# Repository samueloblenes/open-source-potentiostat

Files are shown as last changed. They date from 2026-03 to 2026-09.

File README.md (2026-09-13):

# Open-Source Potentiostat

**A fully open-source, low-cost potentiostat for electrochemical characterization, built as an alternative to commercial instruments.**

> **Status: Active development.** Not yet complete or ready for use. See [Build Progress](#build-progress) below for current status.

---

## Overview

This project is an attempt to build a fully open - hardware, firmware, and software - potentiostat capable of electrochemical characterization, at a fraction of the cost of a comercial instrument.

The instrument is built around a three-electrode electrochemical cell, using a potentiostatic control loop to maintain a precise potential and a switchable-gain transimpedance amplifier to measure the resulting current. A Teensy 4.1 handles low-level control and data acquisition, with a Python-based GUI for control and data analysis.

Once complete, the instrument will be validated against published cyclic voltammetry data.

## Build Progress

- [x] Circuit design
- [x] SPICE simulation
- [x] Preliminary firmware
- [x] Breadboard prototype
- [x] Enclosure design 
- [ ] Breadboard testing & debugging *(in progress)*

<p float="left">
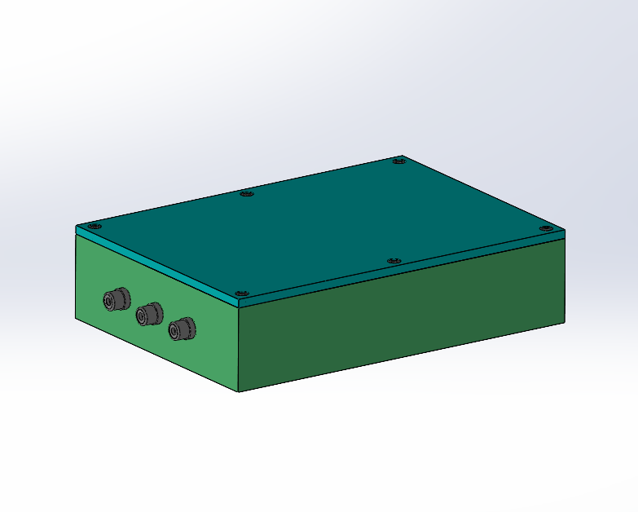
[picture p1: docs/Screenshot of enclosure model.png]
  
</p>

<p float="left">
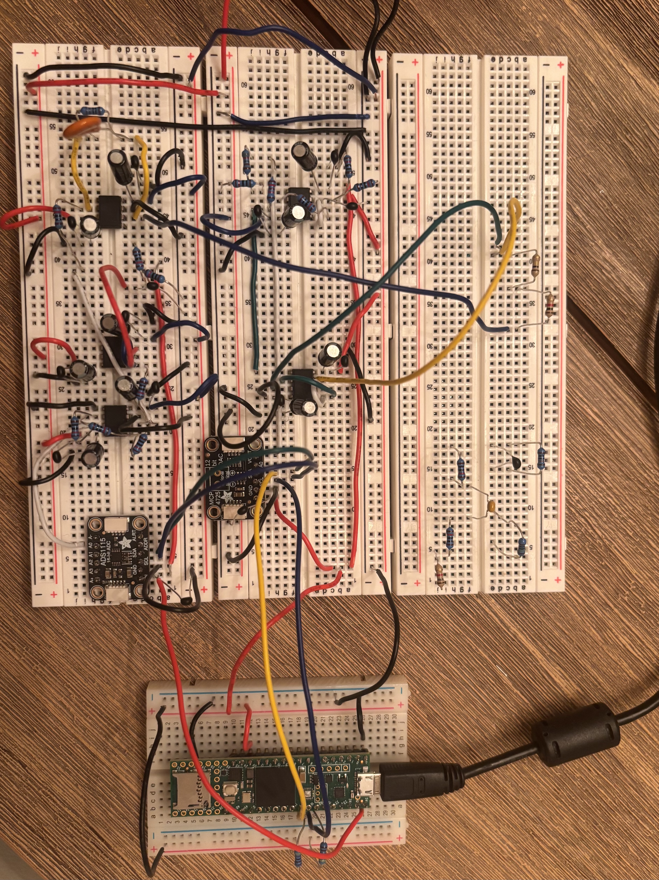
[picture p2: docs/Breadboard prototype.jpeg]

</p>

## Repository Structure
```
open-source-potentiostat/
├── firmware/                
│   └── firmware.ino         
├── hardware/                
│   ├── schematic/           
│   └── simulation/          
├── software/                
│   ├── app.py
│   ├── main.py
│   └── requirements.txt
├── docs/                    
│   ├── BOM.csv
│   ├── circuit_design_notes.md
│   └── simulation_notes.md
├── LICENSE_hardware
├── LICENSE_software
└── README.md
```
## Acknowledgments

This project draws inspiration from **CheapStat**, an open-source, "do-it-yourself" potentiostat originally designed by Aaron Rowe, Andrew Bonham, Michael Zimmer, Kevin Plaxco and colleagues at UC Santa Barbara, which demonstrated that a fully open, low-cost potentiostat could support real analytical and educational applications.

- Rowe, A.A., Bonham, A.J., White, R.J., et al. (2011). ["CheapStat: An Open-Source, 'Do-It-Yourself' Potentiostat for Analytical and Educational Applications."](https://doi.org/10.1371/journal.pone.0023783) *PLOS ONE*.

## License

- Hardware design files: [CERN-OHL-S v2](https://ohwr.org/cern_ohl_s_v2.txt)
- Software and firmware: MIT

## Author

**Samuel O'Blenes**
GitHub: [@samueloblenes](https://github.com/samueloblenes)

---

*This is a work in progress - design files, firmware, and documentation will be updated as the project develops. Feedback and suggestions are welcome via GitHub Issues.*

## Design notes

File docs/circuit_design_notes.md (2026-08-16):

# Component Selection and Circuit Design

## Overview
This document describes the circuit design of the open-source potentiostat, The design priorities are affordability, reproducibility, and sufficient performance.

## Design requirements and constraints

### Functional requirements
CV - Cyclic Voltammetry:
The working electrode potential is swept linearly from an initial value to a final value, then reversed back to the initial value. Current at the working electrode is measured continuously as a function of applied potential. Used for characterizing oxidation and reduction reactions, corrosion behaviour, reaction reversibility, etc.

LSV - Linear Sweep Voltammetry
The working electrode potential is swept linearly from an initial value to a final value in one direction only, with no reverse scan. Current is measured continuously during the sweep.

CA - Chronoamperometry
The working electrode potential is stepped to a value and held constant while current at the working electrode is measured as a function of time. Used for studying reaction kinetics.

### Performance requirements
The instrument must operate within a voltage, current, and scan rate range sufficient to perform the electrochemical techniques described in Section 2.1.

Potential Range:
A potential control range of ±2V was selected to cover all planned experiments with comfortable margin while keeping circuit complexity and cost minimal.

Current Measurement Range:
The working electrode current during the planned experiments spans approximately from 10 nA to 2 mA. Four switchable transimpedance gain ranges (1 kΩ, 10 kΩ, 100 kΩ, 1 MΩ) were selected to cover this range with adequate resolution at each decade.

Resolution and Accuracy:
In order to have sufficient accuracy, the following minimum resolution specifications were established:
- current resolution less than 1 nA
- voltage resolution at least 1 mV
- ADC resolution at least 16-bit
- potential accuracy of ± 5mV

### Cost and accessibility constraints
- Cost should be kept under $200
- Components must be available from major suppliers
- Assembly should be relatively simple and require hand soldering only

## Component selection and circuit design

### Microcontroller

#### Microcontroller consideration
The microcontroller must satisfy the following requirements:
- Sufficient processing speed for precise sweep timing across the full scan rate range of 1 mV/s to 500 mV/s without timing jitter that would distort CV curve measurements.
- Hardware I2C and SPI peripherals for communication with the DAC and ADC.
- A regulated 3.3V output and a 5V output.
- Compatibility with the Arduino IDE to maximise accessibility and reproducibility.

#### Microcontroller selection
The Teensy 4.1 was selected. It operates at 600 MHz with an ARM Cortex-M7 processor, providing sufficient processing speed, and is fully compatible with the Arduino IDE via the Teensyduino add-on. I2C and SPI peripherals are available for communication with the DAC and ADC. The board provides a regulated 3.3V output and a 5V VUSB output. It does not include an onboard DAC; this is addressed through the use of an external I2C DAC, which adds only one low-cost component to the design and has negligible impact on circuit complexity.

### DAC

#### DAC considerations
The Teensy 4.1 microcontroller does not include an onboard DAC, so an external DAC is required. The DAC receives a digital value from the Teensy and generates the analog voltage setpoint applied to the control loop, Vset. The DAC must have sufficient resolution to achieve at least 1mV per step, be able to cover the ±2V potential range, and be compatible with the Teensy 4.1 I2C interface.

#### DAC selection
The MCP4725 12-bit DAC was selected for this design. It operates from the Teensy 4.1's 3.3V supply. At 12-bit resolution over a 0 to 3.3V output range, the voltage step size is:

V = 3.3V / 2^12 = 0.806 mV/step

This meets the sub-mV resolution requirement. It is low cost, widely used and available, and breakout boards are widely available for breadboarding.

#### Bipolar output
The MCP4725 produces a unipolar output from 0V to 3.3V. The instrument must scan across negative potentials, so a bipolar potential range is required. A unipolar-to-bipolar converter circuit is placed between the DAC output and the control loop. A difference amplifier is used to shift and scale the DAC output to the required range.

For this circuit, a TL072 dual op-amp is used, with one channel as the differential amplifier and the other as a buffer for the 1.65V reference voltage.

The reference voltage is derived from an ADR4533 fixed 3.3V precision voltage reference IC, powered directly from the +12V rail. A matched 10kΩ:10kΩ resistor divider on the ADR4533's output sets the 1.65V midpoint, which is then buffered by the second TL072 channel. Per the ADR4533 datasheet, a minimum 0.1µF output capacitor and a 1µF/0.1µF input capacitor pair are required for stability and noise reduction.

Decoupling capacitors (100nF and 10µF) are placed on the ±12V rails to reduce noise, and a 100nF capacitor decouples the buffered reference voltage node.

### Potentiostatic control circuit
The potentiostatic control circuit receives the set voltage from the DAC, Vset, and maintains the potential in the cell at that value. To do this, the design uses another TL072 dual op-amp, with one channel configured as a reference buffer to read the reference electrode's potential without drawing any current from it, and the other as a control amplifier to maintain the potential in the cell equal to Vset.

### Transimpedance amplifier
The current from the working electrode must be converted into voltage so that the ADC can convert it to a digital signal. This is accomplished using a transimpedance amplifier (TIA). An OPA134 op-amp is used for its low input bias current. This is important because input bias current adds a fixed offset error to the measured current, which becomes significant at the nanoampere level. A feedback resistor is connected between the op-amp's inverting input and the output, and sets the transimpedance gain. The output voltage is determined by the product of the input current and the feedback resistance; for smaller currents a larger feedback resistance is required to get a voltage that the ADC can read. Decoupling capacitors (100nF and 10µF) are placed on the ±12V rails to reduce noise. A feedback compensation capacitor connected in parallel with the feedback resistor prevents oscillations caused by the phase shift introduced by cable capacitance. 

#### Gain switching
To accommodate the current ranges specified above, a DG441 quad analog switch allows switching between four feedback resistances of 1 kΩ, 10 kΩ, 100 kΩ, and 1 MΩ. Each switch is controlled by a different GPIO pin on the Teensy; setting a pin high closes the corresponding switch, completing the circuit between the op-amp's inverting input and the desired feedback resistor, which is connected to the output. This circuit is shown in Figure 5.

A 50 pF compensation capacitor is placed in parallel with the feedback resistors to prevent oscillation caused by the phase shift introduced by the input capacitance. This value was determined by AC stability simulation across all four gain ranges.

#### TIA output offset
The TIA output is bipolar, but the ADC requires a unipolar input within its supply range. An offset is applied using a weighted summing amplifier circuit after the TIA.

The first stage is an inverting summing amplifier that adds a 2.5V offset to the TIA output, shifting the signal range upward while inverting its polarity. The second stage is an inverting unity-gain amplifier that restores the correct polarity. The combined effect is a non-inverting +2.5V shift, placing the full output range within the ADC input window.

The 2.5V reference for the summing stage is supplied directly by an ADR4525 fixed 2.5V precision voltage reference IC, powered from the +12V rail. Per the ADR4525 datasheet, a minimum 1.0µF output capacitor and a 1µF/0.1µF input capacitor pair are required for stability.

The 2.5V offset is subtracted in firmware to recover the true current value.

### ADC

#### ADC considerations
The analog-to-digital converter (ADC) digitises the TIA output voltage to be sent to the Teensy 4.1. The ADC must have a resolution of at least 16-bit to achieve the resolution specified above.

#### ADC selection
The ADS1115 16-bit ADC was selected. It shares the I2C bus with the MCP4725 DAC, and operates from the 5V VUSB pin. 

#### I2C pull-up resistors
The SDA and SCL lines require pull-up resistors to 3.3V for correct I2C operation. Two external 4.7 kΩ resistors are placed on the SDA and SCL nets.

### Power supply

#### +12V input and −12V generation
+12V is supplied externally via a barrel-jack input. The −12V rail required by the op-amps is generated from this +12V supply using a TC7662B switched-capacitor voltage inverter.

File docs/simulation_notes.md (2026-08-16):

# Simulation Notes
This document outlines the circuit simulations done during the design process. All simulations were done using LTspice, an open source SPICE simulation software. Simulation files can be found in the `simulations/` folder of this repository.

---

# 1. DAC Offset Circuit

**Purpose**
Verify that the difference amplifier correctly scales and shifts the MCP4725 unipolar output (0–3.3V) to the required bipolar range (±2V), confirming the resistor values R1 = 8.25 kΩ, R2 = 10 kΩ, R3 = 10 kΩ, R4 = 12.1 kΩ produce the correct output.

## 1.1 DC Operating Point

Expected results are calculated as follows:

```
Vout = (R4/R2) × (Vin - Vref)
Vout = (12.1k/10k) × (Vin - 1.65)
Vout = 1.21 × (Vin - 1.65)
```

**Test 1: Minimum input (Vin = 0V)**

Calculation: Vout = 1.22 × (0 - 1.65) = **-2.0V**

| Node | Expected | Simulated | Pass/Fail |
|------|----------|-----------|-----------|
| Vref | 1.65V | 1.64996V | Pass |
| Vout | -2.0V | -1.9997V | Pass |

Simulation file: `DAC_Offset_DC_PNT_1`

---

**Test 2: Midpoint input (Vin = 1.65V)**

Calculation: Vout = 1.22 × (1.65 - 1.65) = **0V**

| Node | Expected | Simulated | Pass/Fail |
|------|----------|-----------|-----------|
| Vref | 1.65V | 1.65V | Pass |
| Vout | 0V | 0.000110925V | Pass |

Simulation file: `DAC_Offset_DC_PNT_2`

---

**Test 3: Maximum input (Vin = 3.3V)**

Calculation: Vout = 1.22 × (3.3 - 1.65) = **+2.0V**

| Node | Expected | Simulated | Pass/Fail |
|------|----------|-----------|-----------|
| Vref | 1.65V | 1.64996V | Pass |
| Vout | 2V | 1.99993V | Pass |

Simulation file: `DAC_Offset_DC_PNT_3`

**Outcome**
The simulation performed as expected to an acceptable degree of error for all 3 cases, correctly offsetting and scaling the DAC output to the required ±2V bipolar range.

---

# 2. Potentiostat Control Loop

**Purpose**
Verify that the potentiostatic control circuit correctly maintains the working electrode potential equal to Vset. The control amplifier (U3) compares Vset against the buffered reference electrode potential from the reference buffer (U2) and drives the counter electrode (CE) to eliminate any error. The error between Vset and V(RE) should be negligible at steady state.

## 2.1 DC Operating Point

**Expected results:**
At steady state with the feedback loop closed, the control amplifier enforces V(RE) = Vset. A resistor is used as a stand-in for a cell connected directly between CE and RE. V(RE) should equal Vset.

**Test 1: 10 kΩ resistor load**

| Node | Expected | Simulated | Pass/Fail |
|------|----------|-----------|-----------|
| Vset | 0.5V | 0.5V | Pass |
| V(CE) | 0.5V | 0.5V | Pass |
| V(RE) | 0.5V | 0.5V | Pass |

Simulation file: `Control_Loop_DC_OP_PNT_1`

---

**Test 2: 20 kΩ resistor load**

| Node | Expected | Simulated | Pass/Fail |
|------|----------|-----------|-----------|
| Vset | 0.5V | 0.5V | Pass |
| V(CE) | 0.5V | 0.5V | Pass |
| V(RE) | 0.5V | 0.5V | Pass |

Simulation file: `Control_Loop_DC_OP_PNT_2`

**Outcome**
The simulation performed as expected for both cases. The circuit correctly maintains V(RE) = Vset regardless of load resistance, confirming correct potentiostatic control loop operation.

---

## 2.2 Control Loop Tracking

**Purpose**
Ensure the counter electrode responds fast enough to keep the reference electrode at the target potential across the full CV scan rate range.

**Simulation Configuration:**
- Input: Vset set to a sine wave, DC Offset = 0V, Amplitude = 2V, Frequency = 10 Hz
- Load: resistor between CE and RE
- Command: `.tran 0 200ms`
- Probe: Vset and V(RE) on the same graph

**Expected Outcome:**
- V(RE) should perfectly overlap Vset
- V(RE) - Vset = 0 at all times
- No clipping

Simulation file: `Control_loop_Trans_1`

**Outcome**
V(RE) and Vset overlapped perfectly with a difference of zero, confirming the control loop tracks the input signal correctly with no lag or clipping at the tested frequency.

---

# 3. Transimpedance Amplifier (TIA)

**Design note:** Over the required current range, the TIA may output a negative voltage. This is an issue for the unipolar ADC so we need to shift the TIA output. This is done after the TIA by a separate summing circuit.

The TIA output voltage before the summing circuit is:

```
Vout_TIA = -(Iin × Rfeedback)
```

After the summing circuit:

```
Vout_final = 2.5 + (Iin × Rfeedback)
```

The 2.5V offset is subtracted in firmware to recover the true current value.

## 3.1 DC Operating Point

**Purpose**
Verify that the TIA correctly converts working electrode current to an output voltage, and that the summing circuit correctly applies the 2.5V offset, according to Vout = 2.5 + (Iin × Rfeedback).

Expected results calculated using: `Vout = 2.5 + (Iin × R)`, with 1 MΩ feedback resistor:

**Test 1: Iin = +2 µA**

Calculation: Vout = 2.5 + (2×10⁻⁶ × 1×10⁶) = **4.5V**

| Node | Expected | Simulated | Pass/Fail |
|------|----------|-----------|-----------|
| V(WE) | 0V | ~0V | Pass |
| Vout | 4.5V | 4.5V | Pass |

Simulation file: `TIA_DC_OP_PNT_1`

---

**Test 2: Iin = 0 µA**

Calculation: Vout = 2.5 + (0) = **2.5V**

| Node | Expected | Simulated | Pass/Fail |
|------|----------|-----------|-----------|
| V(WE) | 0V | ~0V | Pass |
| Vout | 2.5V | 2.5V | Pass |

Simulation file: `TIA_DC_OP_PNT_2`

---

**Test 3: Iin = -2 µA**

Calculation: Vout = 2.5 + (-2×10⁻⁶ × 1×10⁶) = **0.5V**

| Node | Expected | Simulated | Pass/Fail |
|------|----------|-----------|-----------|
| V(WE) | 0V | ~0V | Pass |
| Vout | 0.5V | 0.500003V | Pass |

Simulation file: `TIA_DC_OP_PNT_3`

**Outcome**
The simulation performed as expected for all 3 cases. The TIA correctly converts working electrode current to voltage and the summing circuit correctly applies the 2.5V offset, keeping the output within the ADC input range for the full expected current range.

---

## 3.2 AC Stability Analysis

**Purpose**
Ensure the TIA does not oscillate across all four feedback resistance values.

**Simulation Configuration:**
- Input: AC current source (AC = 1) through a Randles cell model (Rs = 100 Ω, Cdl = 20 µF, Rct = 10 kΩ)
- Command: `.ac dec 100 1 10Meg`
- Probe: TIA output node

**Expected Outcome:**
- Gain flat at low frequencies, rolling off smoothly at high frequencies
- Phase margin between 45° and 90° to prevent oscillation

| Test | Feedback Resistor | Compensation Capacitor | Result |
|------|------------------|----------------------|--------|
| 1 | 1 kΩ | 50 pF | Stable |
| 2 | 10 kΩ | 50 pF | Stable |
| 3 | 100 kΩ | 50 pF | Stable |
| 4 | 1 MΩ | 50 pF | Stable |

Simulation files: `TIA_AC_Stability_1K`, `TIA_AC_Stability_10K`, `TIA_AC_Stability_100K`, `TIA_AC_Stability_1M`

**Outcome**
A compensation capacitor of 50 pF across the feedback resistor ensures TIA stability for all four feedback resistance values. The C1 value in the schematic was updated to 50 pF.

---

## 3.3 Transient Step Response

**Purpose**
Observe how the TIA handles sudden changes in input current and confirm no ringing or instability with the selected compensation capacitor.

**Simulation Configuration:**
- Input: PULSE current source. Parameters: Initial = 0, Pulse = 1 µA, Delay = 1 ms, Rise = 1 ns, Fall = 1 ns, Width = 10 ms, Period = 20 ms
- Command: `.tran 0 50ms 0 10u`
- Probe: TIA output node

**Expected Outcome:**
- When current steps from 0 to 1 µA, Vout should step from 2.5V to 3.5V (2.5V offset + 1 µA × 1 MΩ = 1V swing)
- Signal should settle cleanly with no ringing

| Test | Feedback Resistor | Result |
|------|------------------|--------|
| 1 | 1 kΩ | Pass |
| 2 | 10 kΩ | Pass |
| 3 | 100 kΩ | Pass |
| 4 | 1 MΩ | Pass |

Simulation files: `TIA_Step_1K`, `TIA_Step_10K`, `TIA_Step_100K`, `TIA_Step_1M`

---

## 4. Full-Circuit Randles Cell Simulation

**Purpose**
Verify the complete signal chain with a Randles cell equivalent circuit and confirm that the resulting current-vs-potential response matches the behavior theoretically expected from the Randles cell.

**Simulation Configuration:**

- Randles cell placed between CE and RE/WE: Rs = 100 Ω, Rct = 10 kΩ, Cdl = 10 µF 
- TIA feedback resistor: 1 kΩ
- Input: DAC output/Vin is a PWL sweep, 0V → 3.3V over 1s then 3.3V → 0V over the following 1s
- Command: `.tran 2`
- Probe: V(vset) on the x-axis, (2.5-V(vout))/1k on the y-axis

**Expected Outcome:**

- Since Vset = 1.21 x (Vin - 1.65), the 3.3V/s ramp on Vin produces a Vset scan rate of ≈4.0 V/s
- The response should be dominated by the resistive path in the Randles cell (Rs + Rct), giving a straight line I vs Vset realationshipso with a slope of 1/10.1 kΩ
- The forward and reverse sweep traces should separate into a hysteresis loop, from Cdl charging/discharging (icap = Cdl × dVset/dt)

Calculations, using Vset = ±2V and scan rate = 4.0V/s:

Resistive term (steady-state, Cdl fully charged):
I_R = Vset / (Rs + Rct) = Vset / 10.1kΩ  →  at Vset = 2V: I_R ≈ 198 µA

Capacitive term (icap = Cdl × dVset/dt):
I_C = 10µF × 4.0V/s = 40 µA

Predicted full loop separation: ΔI = 2 × I_C = 80 µA
Predicted forward-branch current at Vset = +2V: I_R + I_C ≈ 238 µA
Predicted reverse-branch current at Vset = +2V: I_R − I_C ≈ 158 µA

| Parameter | Expected Value | 
|------|------------------|
| Total Loop Separation | 80 uA |
| Linear Regression Slope | 9.901e-5 S ~= 99.01 uA/V |
| Forward Y-Intercept | +40 uA |
| Reverse Y-Intercept | -40 uA|

**Results:**

LTSpice simulation plot:

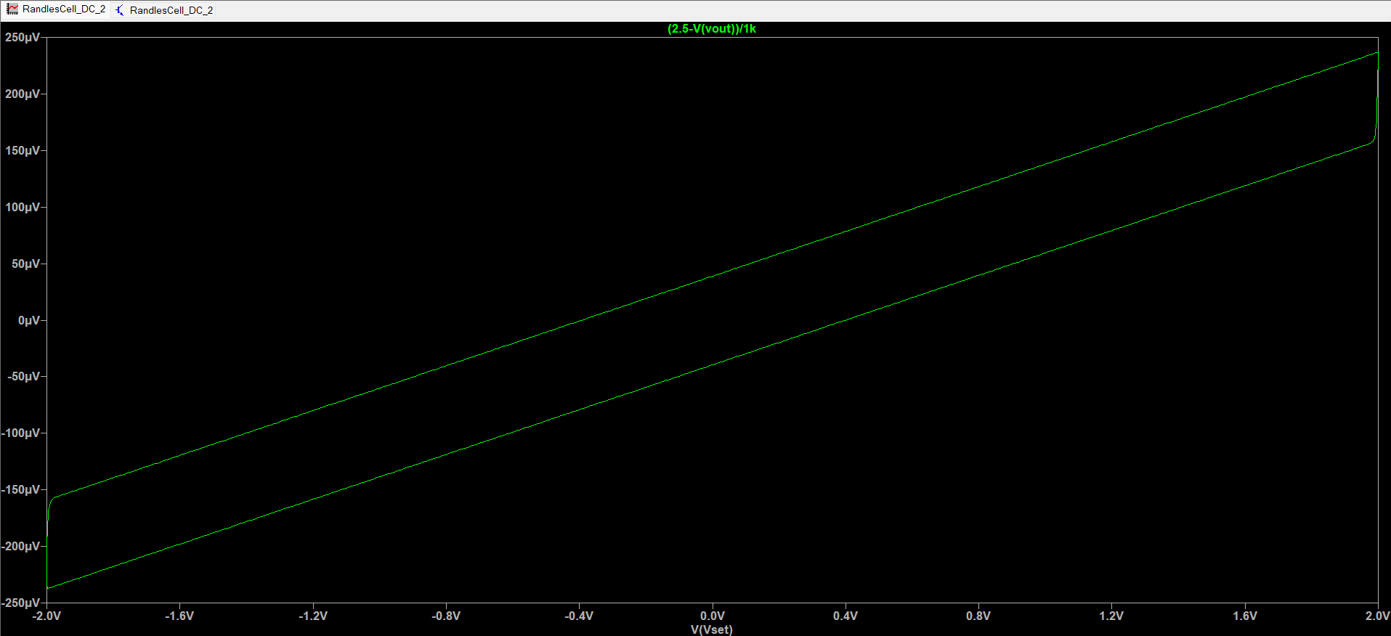
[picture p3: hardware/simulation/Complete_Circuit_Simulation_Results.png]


Linear regression of forward and reverse sweep traces:

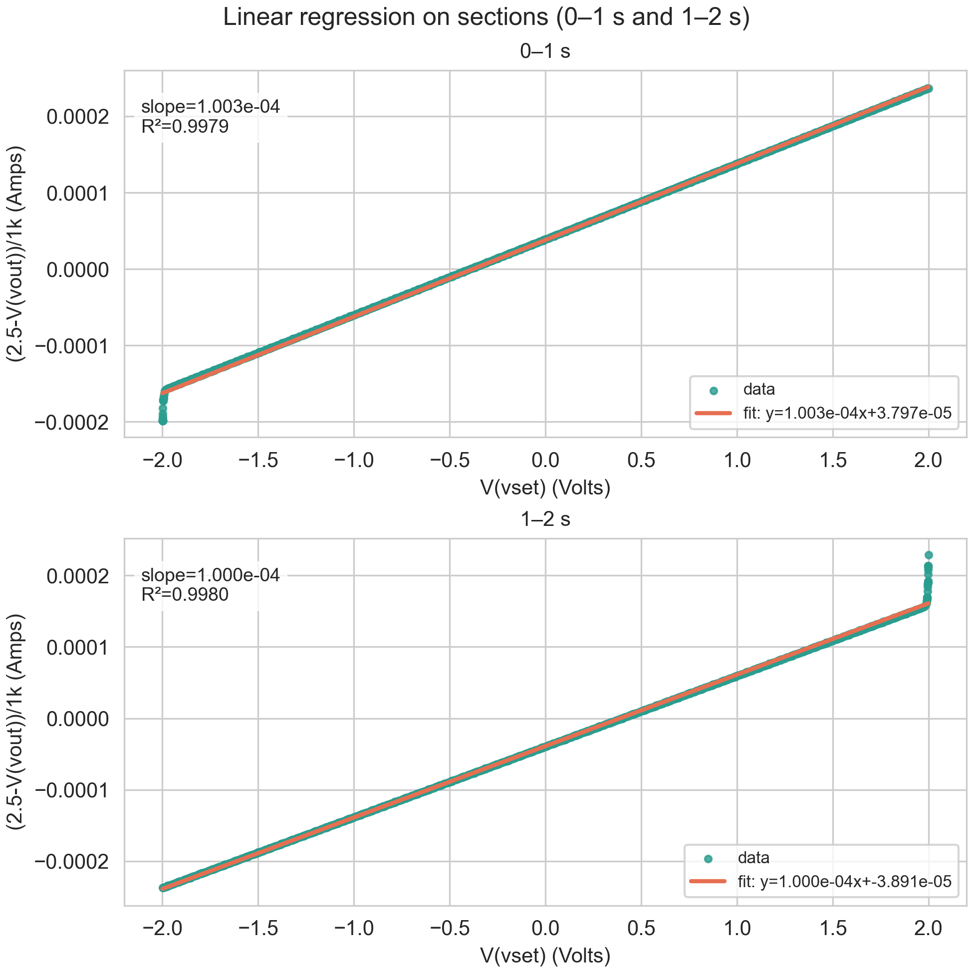
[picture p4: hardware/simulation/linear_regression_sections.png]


Results show a clear hysteresis loop, and linear regression yields a slope within 1% of target ($R^2 \ge 0.998$, $I_{cap} \approx \pm 40\ \mu\text{A}$) with exact theoretical alignment once edge $RC$ transients are trimmed. This confirms the circuit behaves as intended

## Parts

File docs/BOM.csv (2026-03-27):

Reference | Qty | Value
C1 | 1 | 50pF
C2,C5,C6,C7,C9,C10,C12,C13,C14,C15 | 10 | 100nF
C3,C4,C8,C11 | 4 | 10uF
R2,R5,R6,R7,R8,R9,R11 | 7 | 10K
R3 | 1 | 8.25K
R4 | 1 | 12.12K
R10 | 1 | 1K
R12 | 1 | 100K
R13 | 1 | 1Meg
U1 | 1 | OPA134
U2,U4 | 2 | TL072
U3 | 1 | Teensy4.1
U5 | 1 | MCP4725xxx-xCH
U6 | 1 | ADS1115IDGS
U7 | 1 | DG442xY

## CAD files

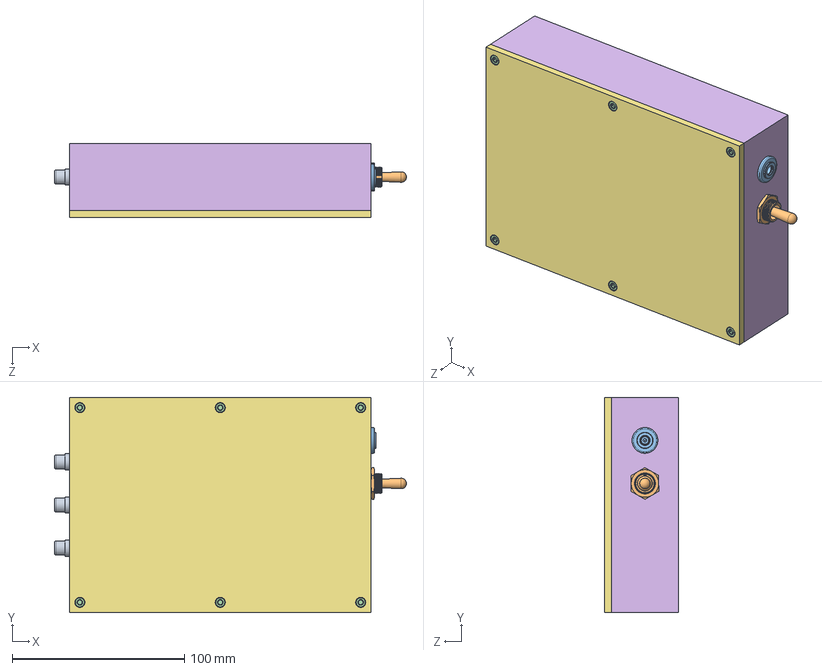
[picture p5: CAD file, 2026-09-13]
hardware/CAD/Enclosure_Assebmly_Rev01.SLDASM
204.3 x 125.0 x 43.0 mm
Enclosure_Lid_Rev01
Enclosure_Bottom_Rev01
94459A434_Heat-Set Inserts for Plastic x 6
91292A111_18-8 Stainless Steel Socket Head Screw x 6
8320N11_Barrel-Style DC Connector
7343K185_Toggle Switch
5432T17_Gold-Plated Brass Panel-Mount Coaxial Connector x 3

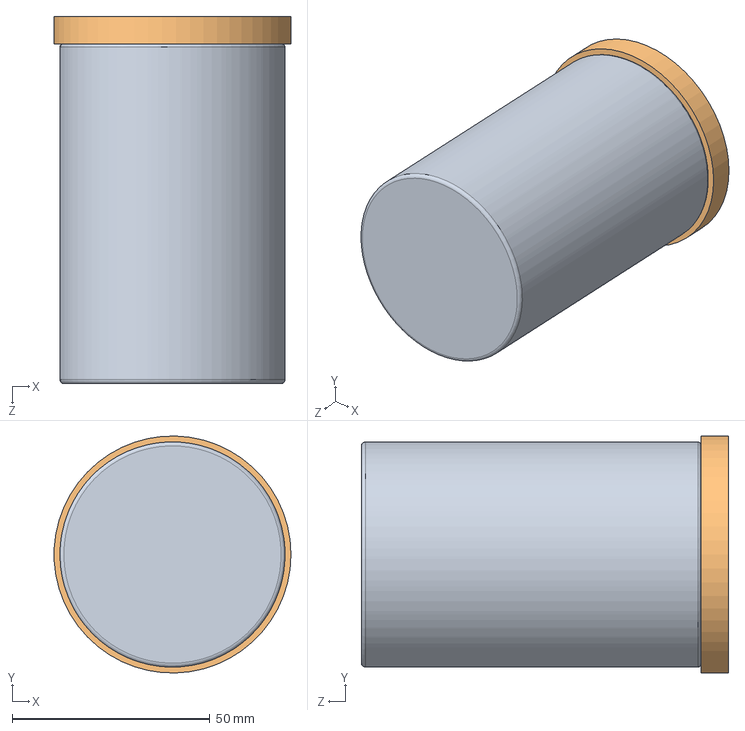
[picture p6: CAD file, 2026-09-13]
hardware/CAD/Cell_Assembly_Rev01.SLDASM
60.0 x 60.0 x 93.0 mm
Electrode_Holder_Rev01
Beaker_model

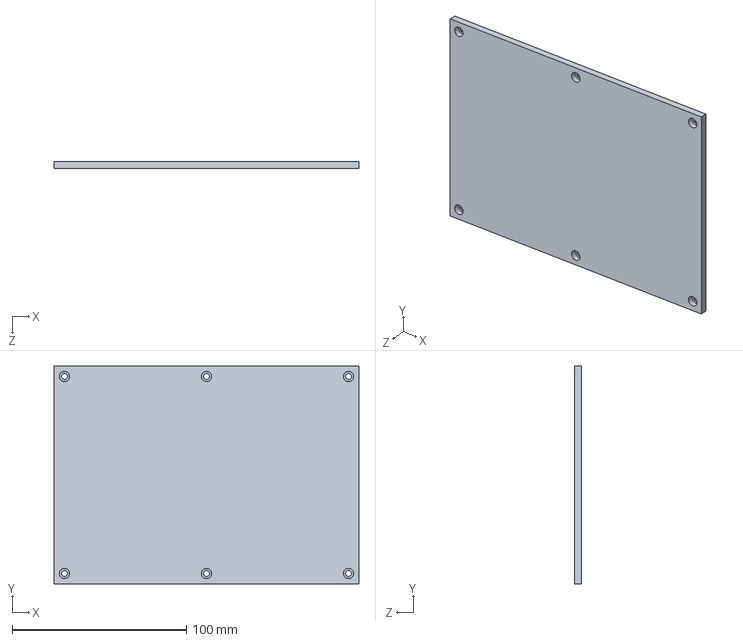
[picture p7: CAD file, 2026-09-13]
hardware/CAD/Enclosure_Lid_Rev01.SLDPRT
175.0 x 125.0 x 4.00 mm

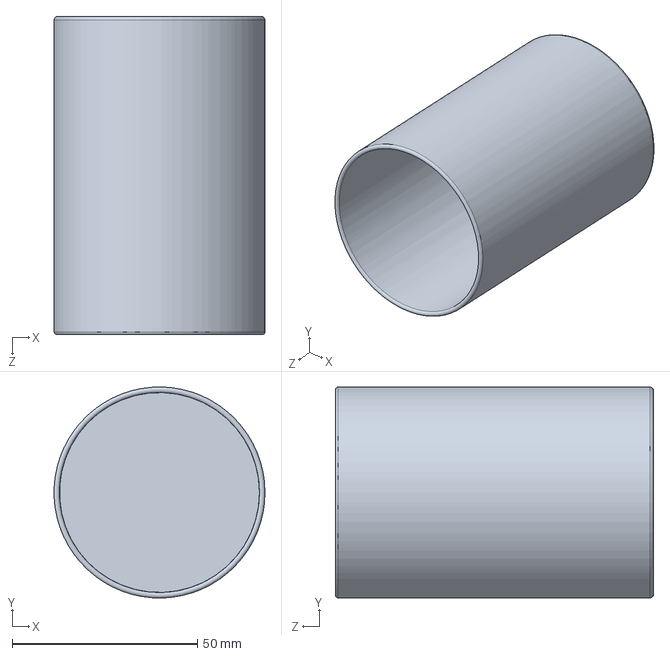
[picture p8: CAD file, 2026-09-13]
hardware/CAD/Beaker_model.SLDPRT
57.0 x 57.0 x 86.0 mm

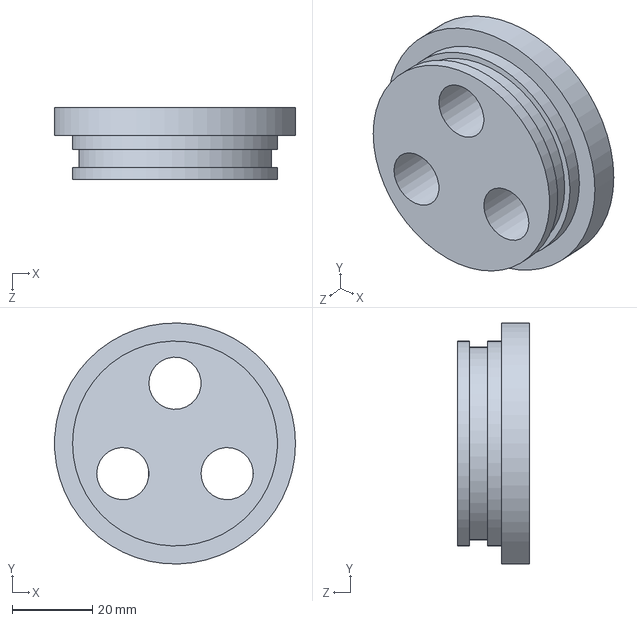
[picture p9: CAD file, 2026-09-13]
hardware/CAD/Electrode_Holder_Rev01.SLDPRT
60.0 x 60.0 x 18.0 mm

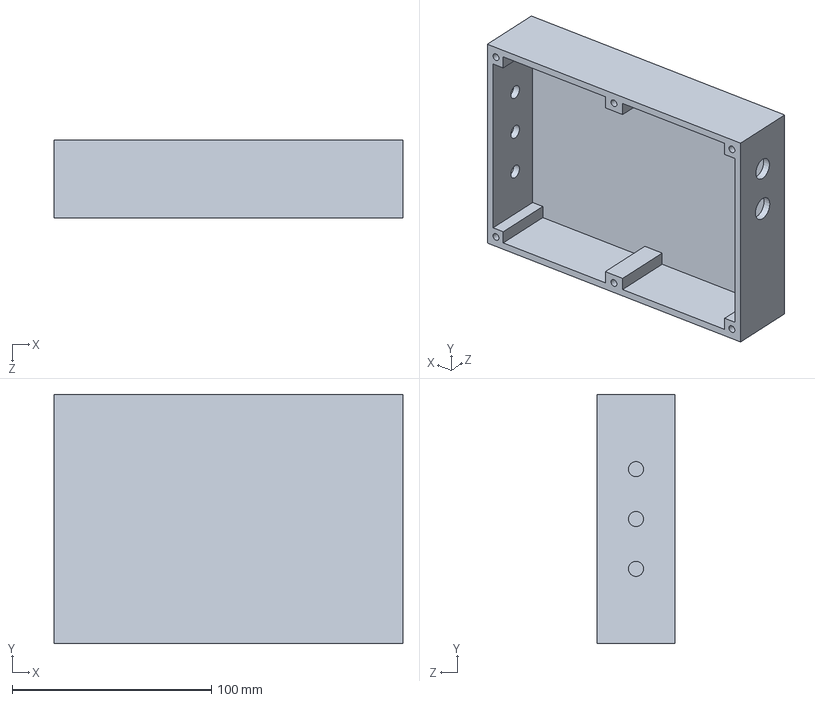
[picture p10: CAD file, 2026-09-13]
hardware/CAD/Enclosure_Bottom_Rev01.SLDPRT
175.0 x 125.0 x 39.0 mm

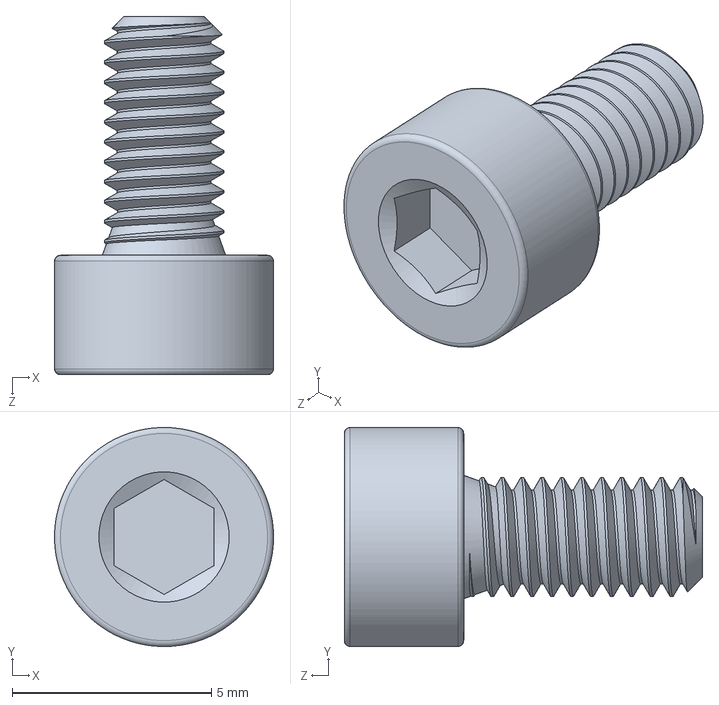
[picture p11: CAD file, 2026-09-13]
hardware/CAD/91292A111_18-8 Stainless Steel Socket Head Screw.SLDPRT
5.50 x 5.50 x 9.00 mm

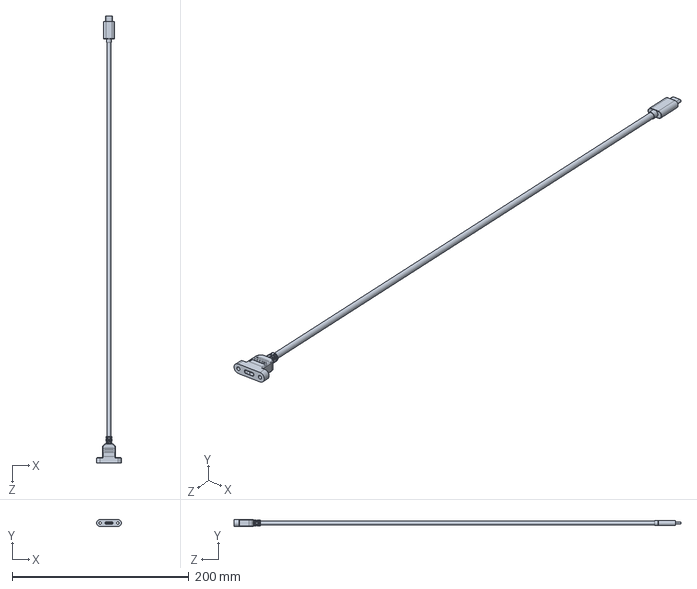
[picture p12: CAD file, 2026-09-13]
hardware/CAD/4872N19_Panel-Mount USB Cord.SLDPRT
28.0 x 8.20 x 506.0 mm

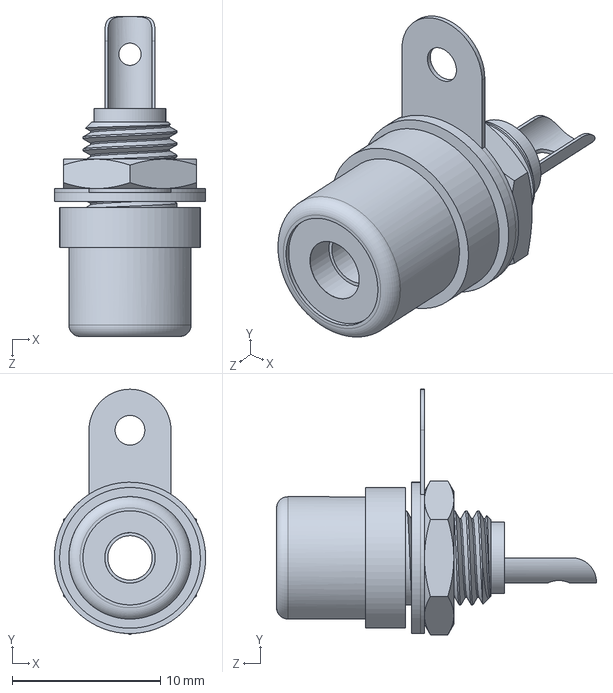
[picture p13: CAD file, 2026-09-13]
hardware/CAD/5432T17_Gold-Plated Brass Panel-Mount Coaxial Connector.SLDPRT
10.2 x 16.6 x 21.6 mm

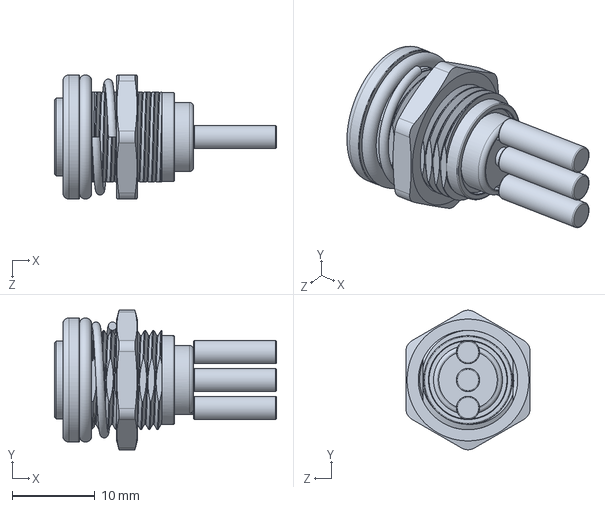
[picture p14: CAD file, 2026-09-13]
hardware/CAD/8320N11_Barrel-Style DC Connector.SLDPRT
26.8 x 16.9 x 15.0 mm

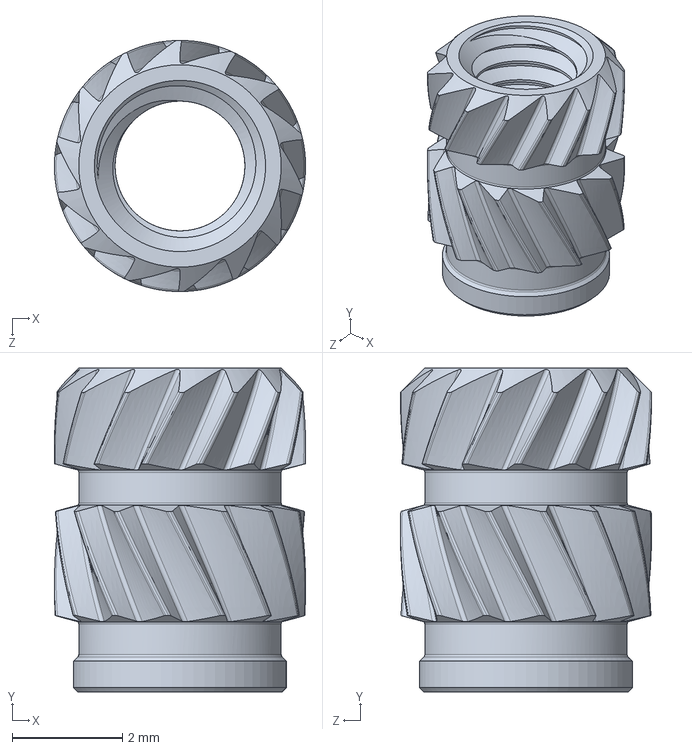
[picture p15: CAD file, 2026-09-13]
hardware/CAD/94459A434_Heat-Set Inserts for Plastic.SLDPRT
4.55 x 5.87 x 4.55 mm

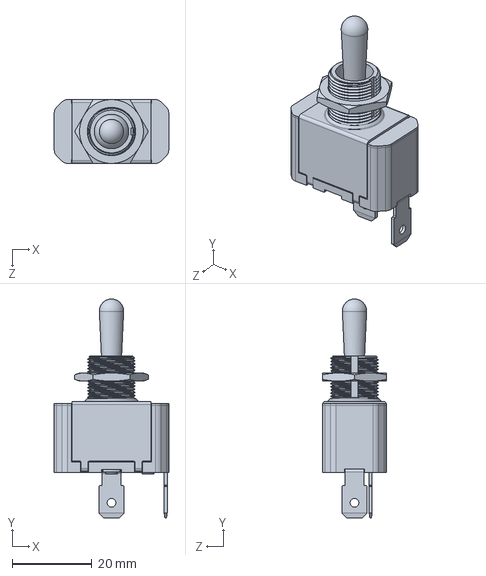
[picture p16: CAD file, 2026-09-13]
hardware/CAD/7343K185_Toggle Switch.SLDPRT
28.7 x 54.9 x 16.0 mm

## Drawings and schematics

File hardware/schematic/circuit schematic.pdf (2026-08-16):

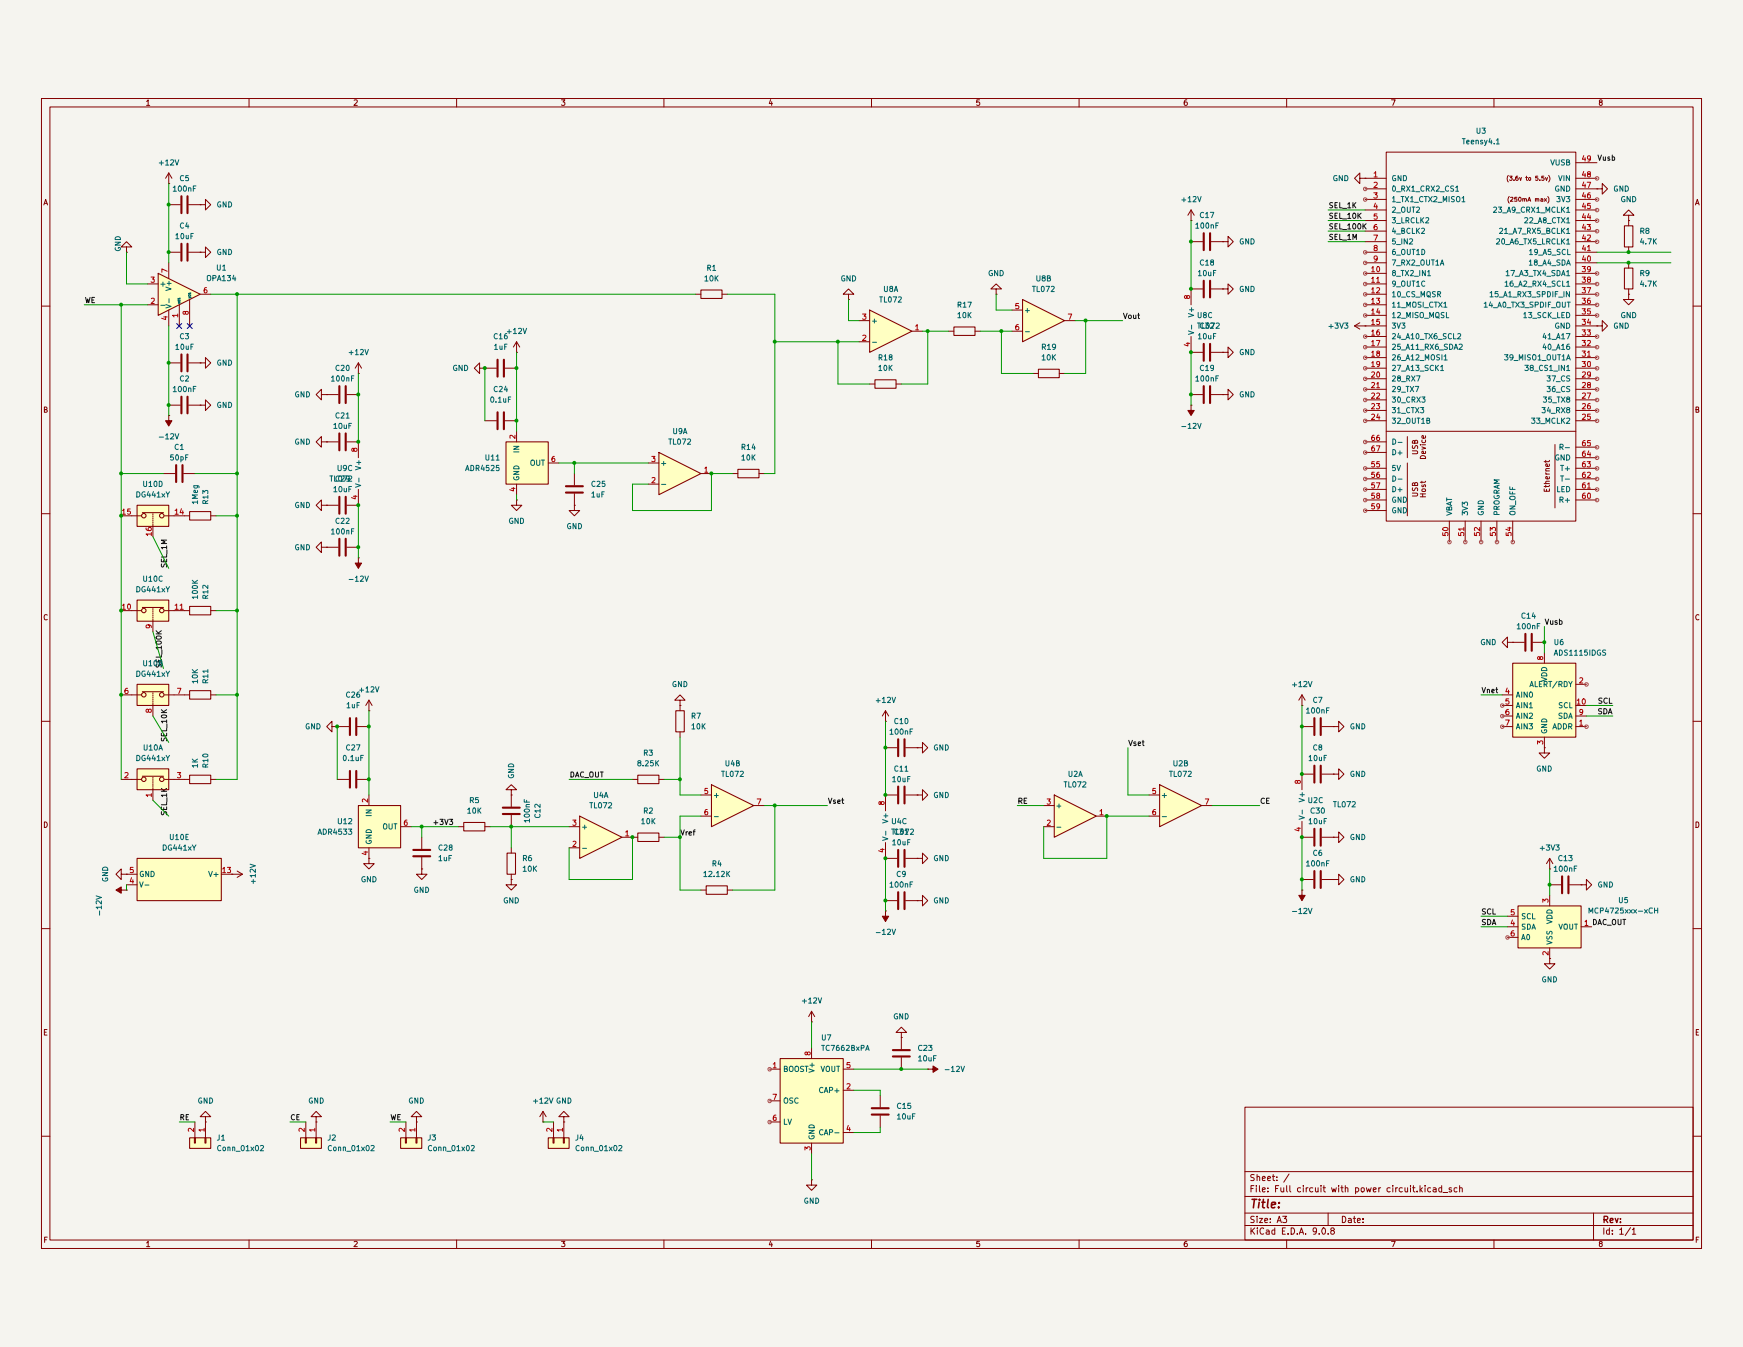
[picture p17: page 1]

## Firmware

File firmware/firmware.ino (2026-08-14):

// =============================================================================
//  Open-Source Potentiostat — Teensy 4.1 Firmware
//  Techniques implemented: CV (Cyclic Voltammetry)
//  Hardware:
//    DAC  — MCP4725 (I2C, addr 0x60)
//    ADC  — ADS1115 (I2C, addr 0x48)
//    TIA  — Fixed gain (gain switching NOT yet implemented)
//    Gain resistor: 100 kΩ (covers ~25 nA – 25 µA range)
//
//  Serial protocol (115200 baud, ASCII, newline-terminated):
//    PC → Teensy   PING
//    Teensy → PC   PONG
//
//    PC → Teensy   CV,<Ei_V>,<Ef_V>,<scanrate_V_per_s>,<cycles>
//                  e.g. CV,-0.5000,0.5000,0.0500,2
//    Teensy → PC   OK
//                  <E_V>,<I_A>,<t_s>   (one line per sample)
//                  DONE
//
//    PC → Teensy   STOP
//    Teensy → PC   (stops sending data; sends nothing extra)
//
//    On any parameter error:
//    Teensy → PC   ERR,<message>
// =============================================================================

#include <Wire.h>

// ── Hardware constants ────────────────────────────────────────────────────────

// I2C addresses
constexpr uint8_t MCP4725_ADDR = 0x62;
constexpr uint8_t ADS1115_ADDR = 0x48;

// MCP4725 write command (fast mode: no EEPROM write)
constexpr uint8_t MCP4725_CMD_FASTWRITE = 0x00;

// ADS1115 register addresses
constexpr uint8_t ADS_REG_CONVERT = 0x00;
constexpr uint8_t ADS_REG_CONFIG  = 0x01;

// ADS1115 configuration written once in setup().
// ALRT and ADDR pins are not used — ADDR is tied to GND (address 0x48),
// ALRT is left unconnected.
//
// Config register layout (written MSB first):
//   [15]    OS=1      start a single-shot conversion immediately
//   [14:12] MUX=100   AIN0 single-ended vs GND
//   [11:9]  PGA=000   ±6.144 V FSR — chosen so the full 0–5 V TIA output
//                     range fits within the ADC input window.
//                     NOTE: the ADS1115 input must not exceed VDD+0.3 V;
//                     with a 5 V supply this is fine.
//   [8]     MODE=1    single-shot (we trigger each conversion manually)
//   [7:5]   DR=100    128 SPS → conversion time ~7.8 ms, simple fixed delay
//   [4:2]             comparator fields — irrelevant, left at reset default (0)
//   [1:0]   COMP_QUE=11  disable comparator output on ALRT pin (reset default)
//
// 128 SPS is chosen over 860 SPS because it allows a simple fixed 8 ms delay
// instead of polling the OS bit, keeping the driver straightforward.
// At the slowest planned scan rate (1 mV/s, dV ~1 mV per step) one sample
// every ~8 ms is more than adequate.
constexpr uint16_t ADS_CONFIG =
    (1      << 15) |   // OS:  start conversion
    (0b100  << 12) |   // MUX: AIN0/GND
    (0b000  <<  9) |   // PGA: ±6.144 V
    (1      <<  8) |   // MODE: single-shot
    (0b100  <<  5) |   // DR:  128 SPS
    (0b11);            // COMP_QUE: disabled (ALRT stays high/floating)

// LSB size for PGA = ±6.144 V: 6.144 V / 32768 counts
constexpr float ADS_LSB_V = 6.144f / 32768.0f;

// Conversion time for 128 SPS with a small safety margin (ms)
constexpr uint8_t ADS_CONV_DELAY_MS = 9;

// DAC (MCP4725): 12-bit over 0–3.3 V
constexpr float DAC_VREF      = 3.3f;
constexpr float DAC_STEPS     = 4096.0f;  // 2^12
constexpr float DAC_LSB_V     = DAC_VREF / DAC_STEPS;

// Unipolar-to-bipolar converter (difference amplifier) transfer function:
//   Vset = GAIN * (Vdac - VREF_DAC)
// From component selection notes:
//   gain  = R4/R2 = 12.12k / 10k = 1.212
//   Vref  = 1.65 V  (half of 3.3 V rail)
constexpr float BIPOLAR_GAIN  = 1.212f;
constexpr float BIPOLAR_VREF  = 1.65f;   // V

// TIA output: Vout = (Iin * Rfeedback) + TIA_OFFSET_V
//   The output is already the correct sign; the +2.5 V offset is a DC shift
//   so the bipolar current signal fits within the ADC input range.
//   Recovery: Iin = (Vout - TIA_OFFSET_V) / Rfeedback  (no sign flip)
constexpr float TIA_OFFSET_V  = 2.5f;
constexpr float TIA_RFEEDBACK = 100000.0f;  // 100 kΩ

// Instrument voltage limits (hard clamp — protects hardware)
constexpr float VSET_MAX_V    =  2.0f;
constexpr float VSET_MIN_V    = -2.0f;

// ── Experiment state ──────────────────────────────────────────────────────────

enum class State { IDLE, RUNNING };
static State gState = State::IDLE;
static bool  gStopRequested = false;

// ── Forward declarations ──────────────────────────────────────────────────────

void      dacWrite(float vset_V);
float     adcRead_V();
float     adcRead_current_A();
void      runCV(float Ei, float Ef, float scanrate, int cycles);
bool      parseCV(const String& cmd, float& Ei, float& Ef,
                  float& scanrate, int& cycles);
void      sendDataPoint(float E_V, float I_A, float t_s);
void      sendError(const char* msg);

// ── Setup ─────────────────────────────────────────────────────────────────────

void setup() {
    Serial.begin(115200);
    Wire.begin();
    Wire.setClock(400000);  // 400 kHz fast-mode I2C

    // Write the ADS1115 config register once at startup.
    // All subsequent reads just trigger a conversion and read the result —
    // no need to reconfigure between reads since PGA, MUX, and data rate
    // don't change during normal operation.
    Wire.beginTransmission(ADS1115_ADDR);
    Wire.write(ADS_REG_CONFIG);
    Wire.write((uint8_t)(ADS_CONFIG >> 8));
    Wire.write((uint8_t)(ADS_CONFIG & 0xFF));
    Wire.endTransmission();

    // Drive DAC to mid-rail (Vset = 0 V) on startup
    dacWrite(0.0f);
}

// ── Main loop ─────────────────────────────────────────────────────────────────

void loop() {
    if (!Serial.available()) return;

    String line = Serial.readStringUntil('\n');
    line.trim();
    if (line.length() == 0) return;

    // ── PING ─────────────────────────────────────────────────────────────────
    if (line == "PING") {
        Serial.println("PONG");
        return;
    }

    // ── STOP ─────────────────────────────────────────────────────────────────
    if (line == "STOP") {
        gStopRequested = true;
        // The running experiment checks gStopRequested and exits cleanly.
        return;
    }

    // ── CV ───────────────────────────────────────────────────────────────────
    if (line.startsWith("CV,")) {
        if (gState == State::RUNNING) {
            sendError("experiment already running");
            return;
        }

        float Ei, Ef, scanrate;
        int   cycles;
        if (!parseCV(line, Ei, Ef, scanrate, cycles)) return;  // error already sent

        gStopRequested = false;
        gState = State::RUNNING;
        Serial.println("OK");
        runCV(Ei, Ef, scanrate, cycles);
        gState = State::IDLE;

        if (!gStopRequested) {
            // Experiment completed naturally — return electrode to 0 V
            dacWrite(0.0f);
            Serial.println("DONE");
        }
        // If stopped mid-run, do not send DONE (the PC already knows via STOP)
        dacWrite(0.0f);
        return;
    }

    // ── Unknown command ───────────────────────────────────────────────────────
    sendError("unknown command");
}

// =============================================================================
//  CV Implementation
// =============================================================================

// runCV — executes a complete cyclic voltammetry sweep.
//
// Parameters:
//   Ei       : initial potential  (V vs RE)
//   Ef       : final/vertex potential (V vs RE)
//   scanrate : potential scan rate (V/s), positive value
//   cycles   : number of complete cycles (Ei → Ef → Ei counts as one cycle)
//
// Each cycle consists of two legs:
//   Forward leg: Ei → Ef
//   Reverse leg: Ef → Ei
//
// The step interval is calculated so that the DAC advances by exactly one LSB
// per step. The ADC is read once per step and the result is sent immediately.
void runCV(float Ei, float Ef, float scanrate, int cycles) {
    // Step size: one DAC LSB mapped back to volts at the cell.
    // Vset = GAIN * (Vdac - Vref), so:
    //   dVset = GAIN * dVdac = GAIN * DAC_LSB_V
    const float dV_step = BIPOLAR_GAIN * DAC_LSB_V;  // ~0.976 mV

    // Time between steps (µs) derived from scan rate and voltage step size.
    //   step_interval = dV_step / scanrate   (in seconds)
    const float step_interval_s  = dV_step / scanrate;
    const uint32_t step_us       = (uint32_t)(step_interval_s * 1e6f);

    // Clamp step_us to a minimum that allows the ADC to complete a conversion.
    // At 128 SPS with a 9 ms safety margin, each read takes ~9 ms minimum.
    const uint32_t MIN_STEP_US = 9000;
    const uint32_t actual_step_us = max(step_us, MIN_STEP_US);

    // Recalculate effective dV if clamped (scan rate limited by ADC speed)
    // We keep dV_step fixed at one DAC LSB and just accept the slower rate.
    // The true scan rate sent back to the PC is implicit in the (E, t) pairs.

    // Experiment start time (reference for all reported timestamps)
    const uint32_t t0_us = micros();

    for (int cycle = 0; cycle < cycles; cycle++) {
        // ── Forward leg: Ei → Ef ─────────────────────────────────────────────
        {
            float V     = Ei;
            float V_end = Ef;
            float sign  = (Ef >= Ei) ? +1.0f : -1.0f;

            while ((sign > 0 && V <= Ef) || (sign < 0 && V >= Ef)) {
                if (gStopRequested) return;

                dacWrite(V);

                uint32_t step_start = micros();

                float I_A = adcRead_current_A();
                float t_s = (float)(micros() - t0_us) * 1e-6f;

                sendDataPoint(V, I_A, t_s);

                // Busy-wait for remainder of step interval
                while ((micros() - step_start) < actual_step_us) {}

                V += sign * dV_step;
            }
            // Ensure the vertex potential is hit exactly
            dacWrite(Ef);
            {
                float I_A = adcRead_current_A();
                float t_s = (float)(micros() - t0_us) * 1e-6f;
                sendDataPoint(Ef, I_A, t_s);
            }
        }

        // ── Reverse leg: Ef → Ei ─────────────────────────────────────────────
        {
            float V    = Ef;
            float sign = (Ei >= Ef) ? +1.0f : -1.0f;

            while ((sign > 0 && V <= Ei) || (sign < 0 && V >= Ei)) {
                if (gStopRequested) return;

                dacWrite(V);

                uint32_t step_start = micros();

                float I_A = adcRead_current_A();
                float t_s = (float)(micros() - t0_us) * 1e-6f;

                sendDataPoint(V, I_A, t_s);

                while ((micros() - step_start) < actual_step_us) {}

                V += sign * dV_step;
            }
            // Ensure Ei is hit exactly at end of cycle
            dacWrite(Ei);
            {
                float I_A = adcRead_current_A();
                float t_s = (float)(micros() - t0_us) * 1e-6f;
                sendDataPoint(Ei, I_A, t_s);
            }
        }
    }
}

// =============================================================================
//  DAC — MCP4725
// =============================================================================
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

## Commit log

2026-03-18 Add notes for PCB CAD file and schematic PDF
2026-03-18 Add notes for PCB design files
2026-03-18 Add notes for enclosure step and STL files
2026-03-18 Create notes file for BOM materials and sourcing
    Added notes on materials and sourcing tips.
2026-03-18 Add step-by-step assembly instructions to build guide
2026-03-24 Update README with project details and status
    Added project overview, current status, repository structure, license, disclaimer, and author information.
2026-03-24 Fix formatting in README for circuit design status
2026-03-24 Add Component Selection and Circuit Design Notes
    This document outlines the circuit design and component selection for the open-source potentiostat, focusing on affordability and performance.
2026-03-24 Rename Component Selection and Circuit Design Notes to Component Selection and Circuit Design Notes.md
2026-03-24 Update Component Selection and Circuit Design Notes.md
2026-03-24 Add component selection and circuit design section
    Added section on component selection and circuit design.
2026-03-24 Document microcontroller and DAC selection details
    Added detailed considerations and selections for microcontroller and DAC components, including specifications and circuit design notes.
2026-03-24 Expand circuit design notes with detailed sections
    Added detailed descriptions for the potentiostatic control circuit, transimpedance amplifier, gain switching, unipolar output, and ADC considerations including selection.
2026-03-24 Update power supply notes for opamps and gain switching
    Clarified power supply requirements for opamps and gain switching.
2026-03-24 Clean up BOM.csv by removing unused columns
    Removed unused columns from BOM and fixed formatting.
    [BOM.csv]
2026-03-24 Fix formatting issue in BOM.csv
    [BOM.csv]
2026-03-24 Add SPICE simulations and update KiCad project
    Add more spice simulation files and images. update schematic with determined TIA capacitance value to keep it stable
2026-03-27 Rename hardware/schematics/Component Selection and Circuit Design Notes.md to docs/Component Selection and Circuit Design Notes.md
2026-03-27 Rename Component Selection and Circuit Design Notes.md to circuit_design_notes.md
2026-04-03 updated circuit notes
2026-04-30 Update Breadboard prototype status to 'In progress'
2026-04-30 update current status
